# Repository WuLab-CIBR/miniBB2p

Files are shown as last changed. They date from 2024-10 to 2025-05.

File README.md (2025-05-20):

# miniature Bessel-beam two-photon microscope (miniBB2p)
## Description
This repository includes the optical design files, technical drawings, assembly protocol, and code for hardware control of miniBB2p. miniBB2p is a head-mounted miniature Bessel-beam two-photon microscope, published in Qian, et al.,"High-throughput two-photon volumetric brain imaging in freely moving mice (2024)". The miniBB2p is characterized by its lightweight design, reduced tethering stress, simple optics, and maximized fluorescence collection efficiency. 
## Contents
1) [Optical design files](https://github.com/WuLab-CIBR/miniBB2p/tree/main/Supplementary%20Data/Zemax)
   
    Bessel beam simplifies the optical design in miniBB2p:
   
   

2) Technical drawings ([2D models](https://github.com/WuLab-CIBR/miniBB2p/tree/main/Supplementary%20Data/2D%20model) and [3D models](https://github.com/WuLab-CIBR/miniBB2p/tree/main/Supplementary%20Data/3D%20model))

     3D models (and 2D drawings for custom components) of all components for bulding a miniBB2p headpiece.
    3D model

3) [Assembly protocol](https://github.com/WuLab-CIBR/miniBB2p/tree/main/Supplementary%20Data/Assembly%20protocol)

     This protocol includes all steps to assemble a miniBB2p headpiece. Each protocol starts with a short-list of main reagents and tools needed, followed by an overview schematic of the module, and a table with the main products.  2D drawings for custom components used in assembly setup are also attached.

4) [Code for hardware control](https://github.com/WuLab-CIBR/miniBB2p/tree/main/Supplementary%20Data/Code)

     An application to control the miniBB2p, set the imaging parameter, and save the imaging data. The application was written with Matlab.

## References
  Qian, L., Liu, Y., Chen, Y., & Wu, J. (2024). High-throughput two-photon volumetric brain imaging in freely moving mice. bioRxiv, 2024-10.
  DOI:https://doi.org/10.1101/2024.10.13.618106

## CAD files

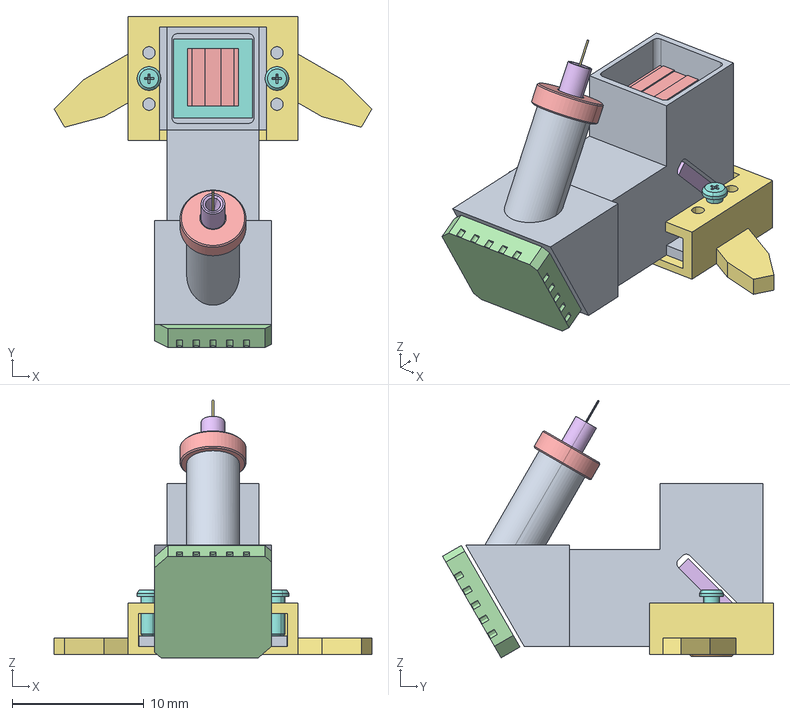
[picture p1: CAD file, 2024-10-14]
Supplementary Data/3D model/miniBB2p.stp
24.1 x 25.1 x 19.5 mm

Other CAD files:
Supplementary Data/Assembly protocol/Technical drawings of the assembly setup/Main Frame Holder.dwg
Supplementary Data/2D model/Main Frame.dwg
Supplementary Data/2D model/Scan and Tube Lens Holder.dwg
Supplementary Data/Assembly protocol/Technical drawings of the assembly setup/MEMS Mirror Holder.dwg
Supplementary Data/2D model/Objective Holder.dwg
Supplementary Data/Assembly protocol/Technical drawings of the assembly setup/Collimator Holder.dwg
Supplementary Data/2D model/Collimator Lens Holder.dwg
Supplementary Data/2D model/Baseplate.dwg

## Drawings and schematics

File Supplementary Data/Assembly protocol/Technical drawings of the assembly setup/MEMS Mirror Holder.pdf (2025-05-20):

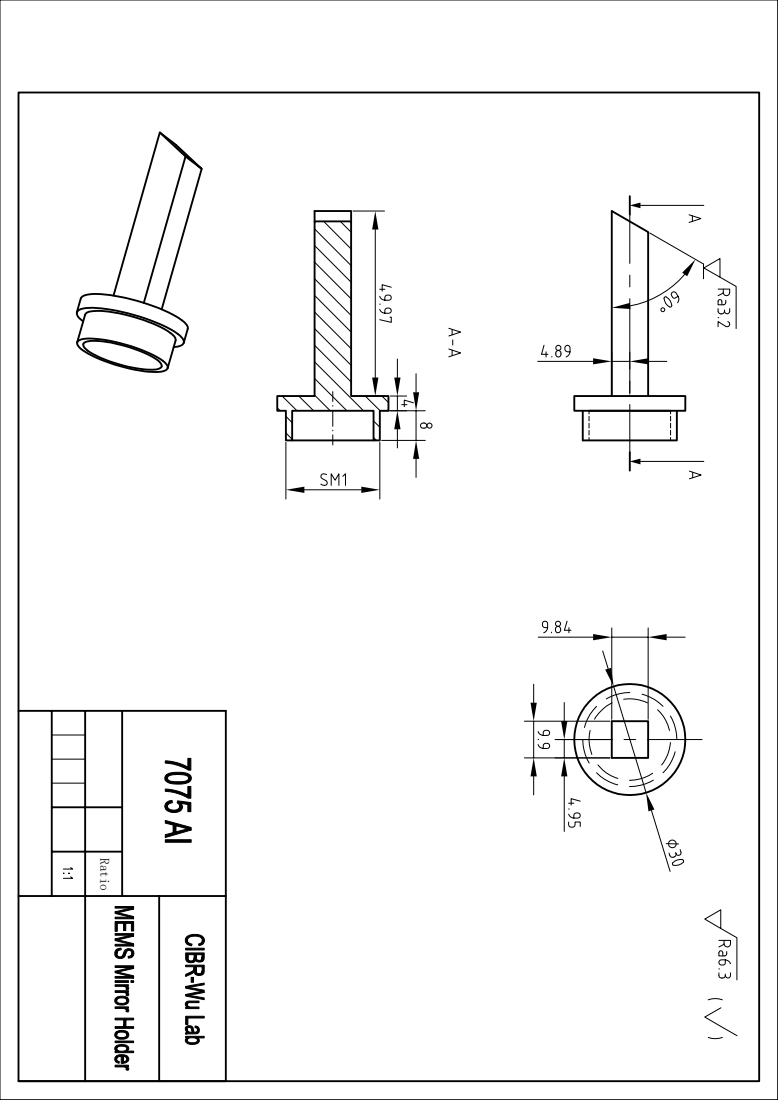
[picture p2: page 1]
Ratio

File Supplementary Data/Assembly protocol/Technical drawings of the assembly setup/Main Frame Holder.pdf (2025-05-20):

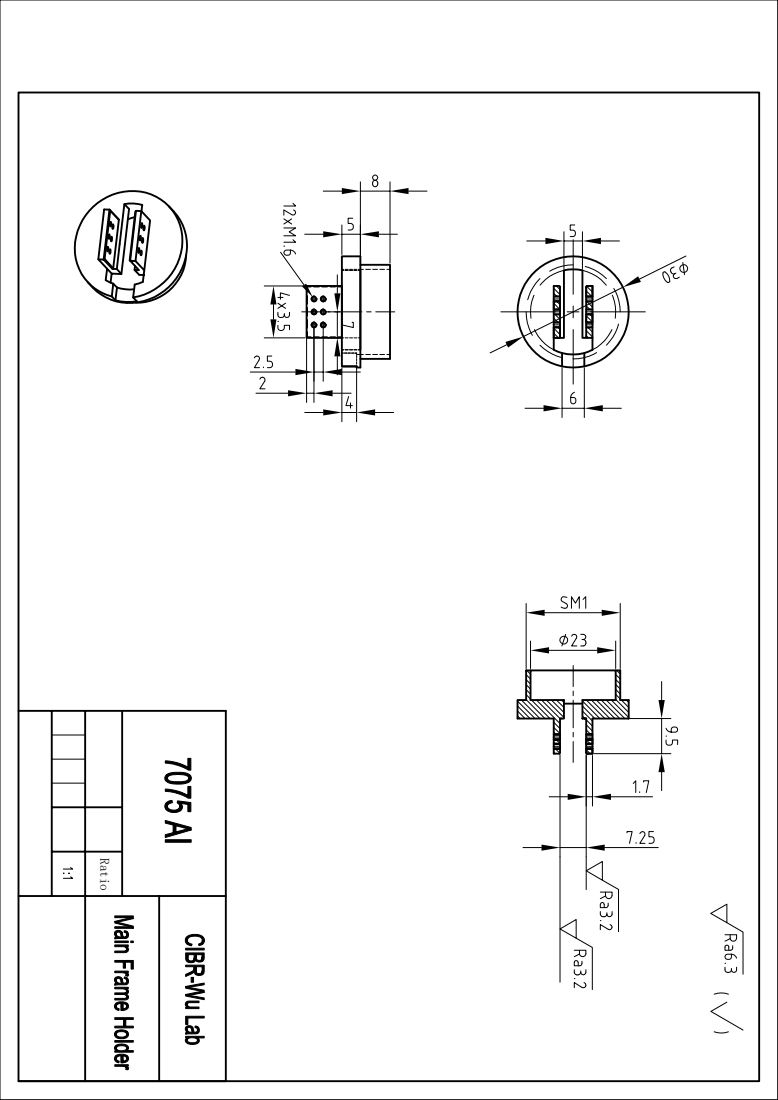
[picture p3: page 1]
Ratio

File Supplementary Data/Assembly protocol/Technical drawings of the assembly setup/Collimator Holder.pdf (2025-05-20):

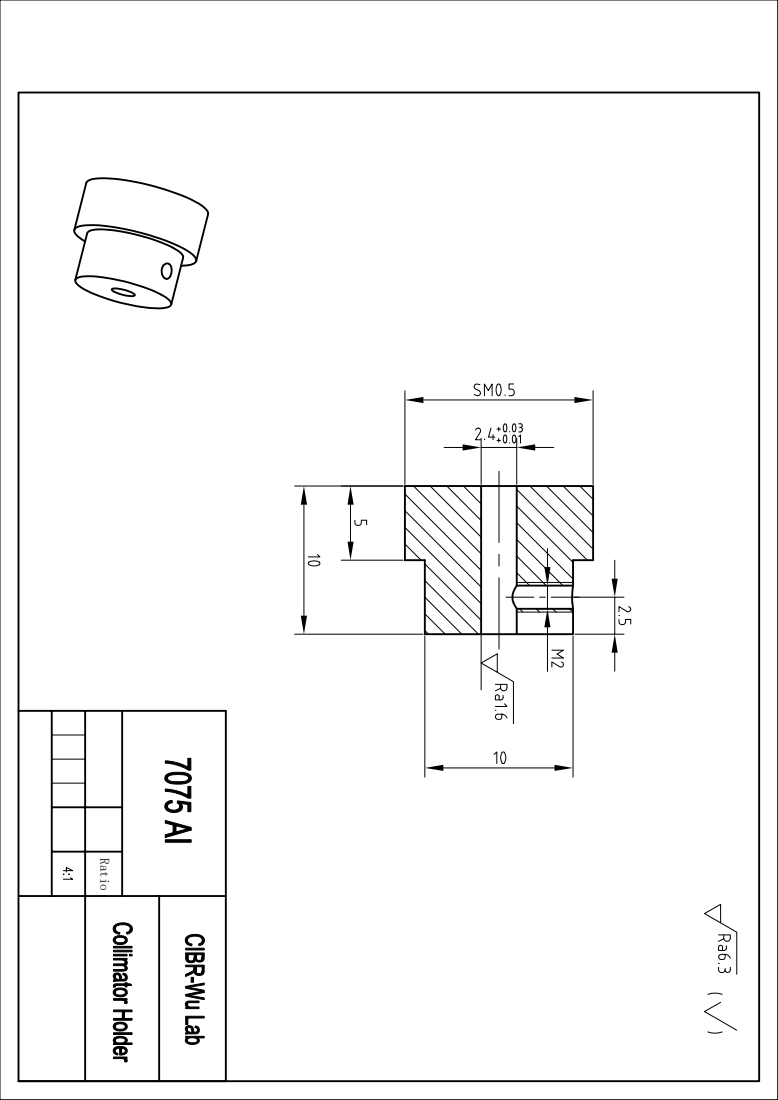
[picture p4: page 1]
Ratio

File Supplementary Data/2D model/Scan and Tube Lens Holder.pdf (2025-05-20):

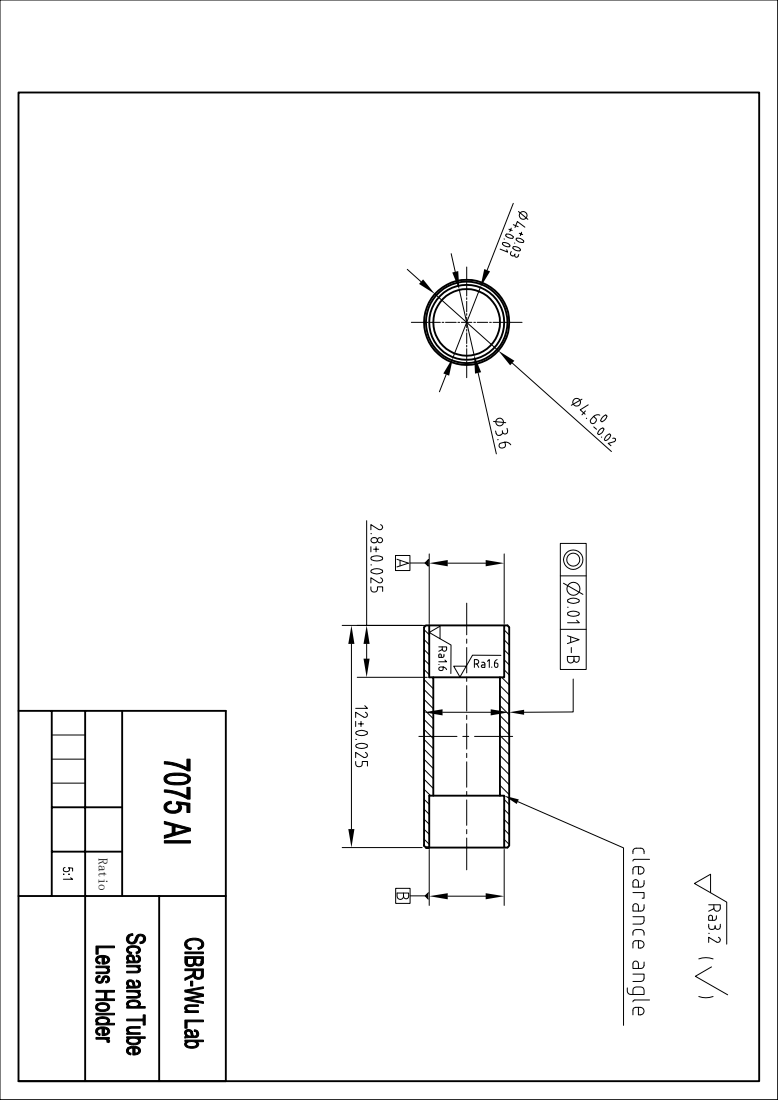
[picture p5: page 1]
Ratio

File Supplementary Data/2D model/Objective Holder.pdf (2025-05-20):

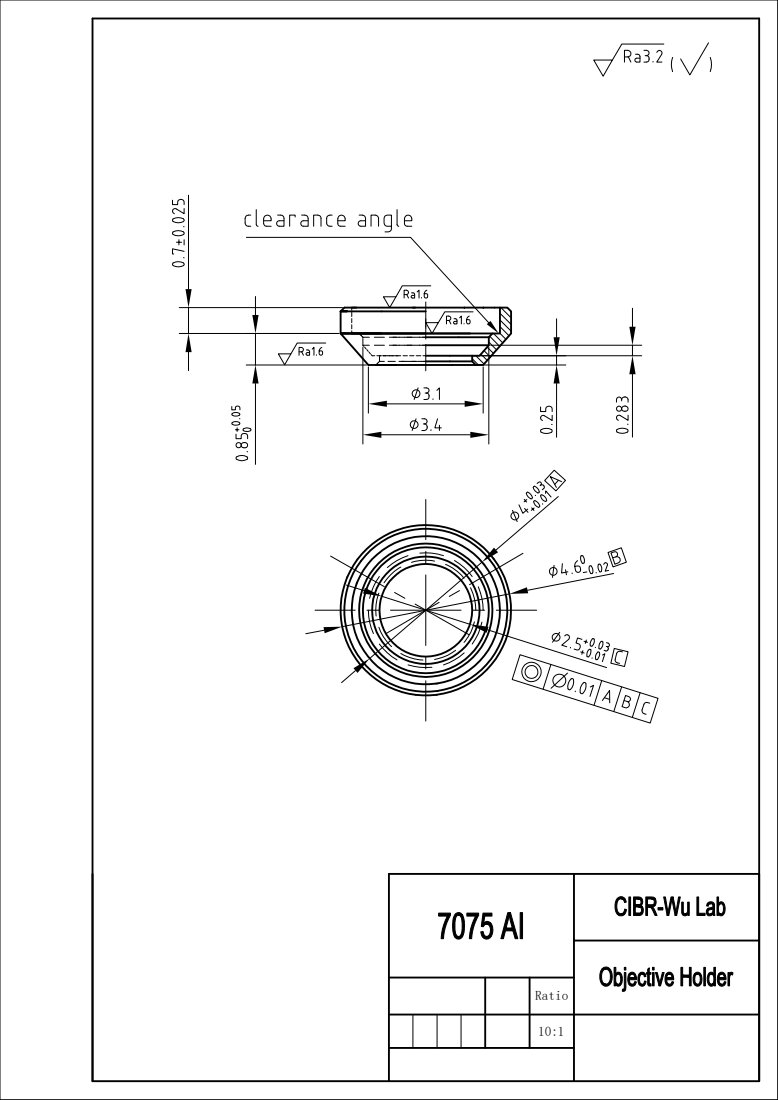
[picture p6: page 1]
Ratio

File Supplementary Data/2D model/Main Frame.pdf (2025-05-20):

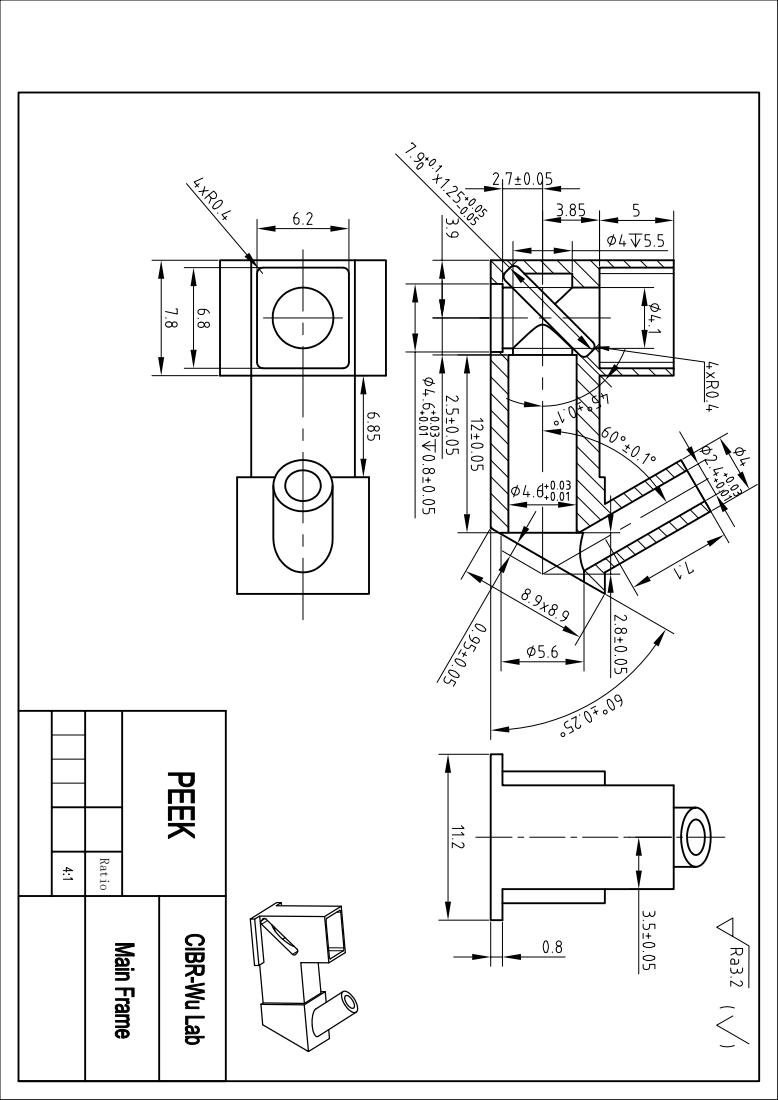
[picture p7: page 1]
Ratio

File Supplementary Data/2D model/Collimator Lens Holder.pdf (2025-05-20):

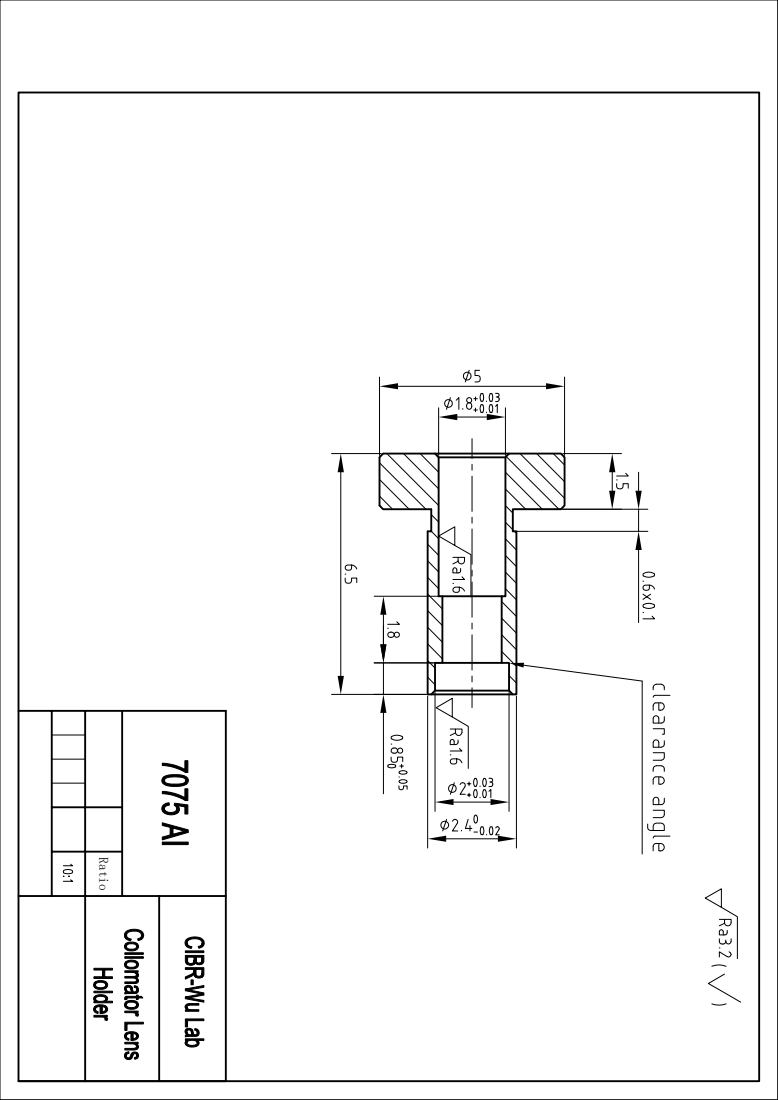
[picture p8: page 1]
Ratio

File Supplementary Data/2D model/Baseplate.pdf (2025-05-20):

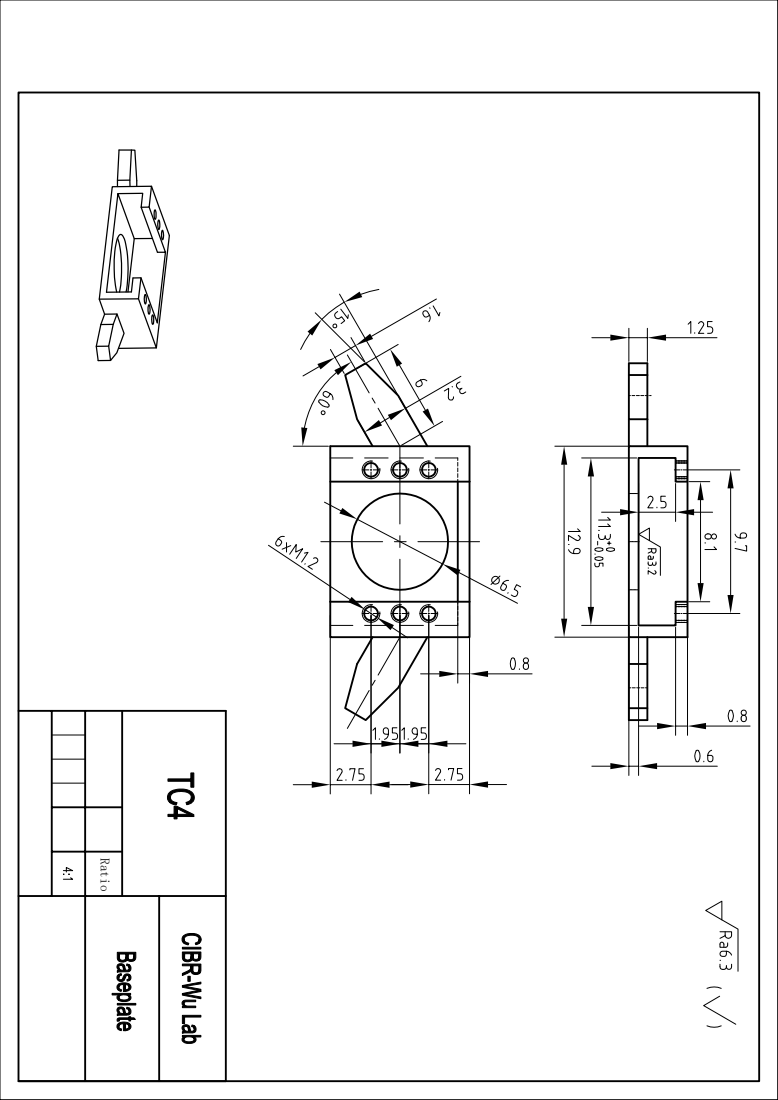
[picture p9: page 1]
Ratio

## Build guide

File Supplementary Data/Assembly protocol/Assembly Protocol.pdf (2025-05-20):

### A protocol for the assembly of miniBB2p headpiece

Part A: Evaluating the micro-axicon fabricated on the fiber tip

Reagents:

⚫ | Air duster
⚫ | Lens cleaning wipe
⚫ | 100% ethanol

Equipment:

⚫ | ~1.5-meter LMA-12 fiber (NKT Photonics) with customized micro-axicon tip (Comcore)
⚫ | Tweezers
⚫ | Fiber stripping tool (T06S13, Thorlabs)
⚫ | Fiber cleaver (CT-101, Fujikura)
⚫ | Stereoscope (M125C, Leica)
⚫ | Beam profiler (CMOS-1202, CINOGY Technologies)
⚫ | Power meter (PM130D, Thorlabs)
⚫ | Others (Table 1)

Table 1 Main components used to evaluate the micro-axicon fabricated on the fiber tip

Component Number | Component Name | Part Number | Amount | Company
#1 | Post-Mountable Fiber Clamp | T711/M-250 | 1 | Thorlabs

#2 | 3-Axis Stage | MAX313D/M | 1 | Thorlabs

#3 | Fiber Holder for 3-Axis Stage | HFV002 | 1 | Thorlabs

Procedure:

Step 1. Examine the fiber tip under a stereoscope to confirm the micro-axicon's quality (Figure 1.1). Should dust be present, carefully clean the tip with either an air duster or a lens cleaning wipe.

Caution! The fiber tip is fragile. Clean it with extreme caution, particularly when using a lens cleaning wipe moistened with 100% ethanol.

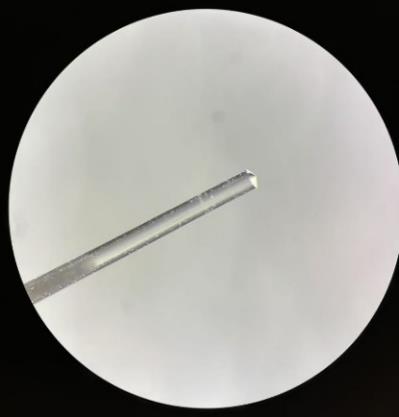
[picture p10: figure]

Figure 1.1 Visual inspection of the fiber tip under the stereoscope

Step 2. Remove about 3–4 cm protecting claddings of the fiber on the other end by using a fiber stripping tool. Then clean the exposed area with a lens tissue moistened with 100% ethanol.
Step 3. Cleave the fiber end using the fiber cleaver (Figure 1.2).

Caution! In Steps 2–3, only handle the fiber end without micro-axicon and avoid any collision/scratch of micro-axicon tip.

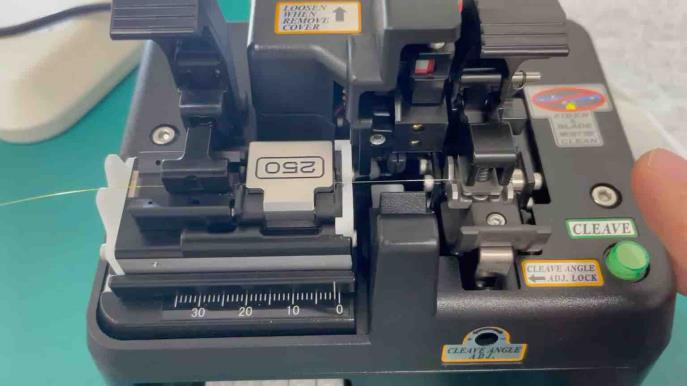
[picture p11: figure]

Figure 1.2 Cleave the fiber end

Step 4. Mount the fiber end with micro-axicon using fiber clamp (#1) and place a power meter behind the micro-axicon. Secure the other end of the fiber on the fiber holder (#2) and mount the holder into a 3-axis stage (#3) (Figure 1.3). Adjust the stage until the output power reaches about several mW.

Note! We do not need to maximize the laser power coupled into the fiber at this step, a power level of several mW is sufficient for the evaluation.

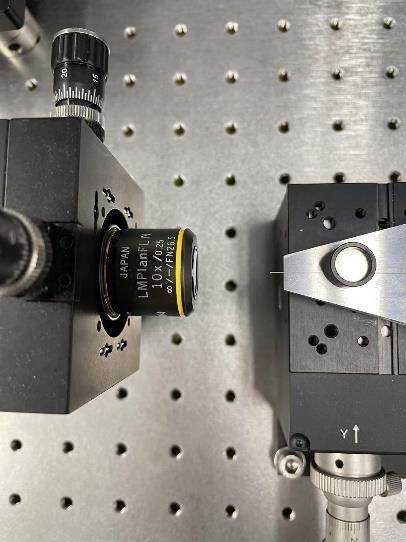
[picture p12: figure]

Figure 1.3 Fiber coupling setup

Step 5. Replace the power meter with the beam profiler in Step 4. Monitor the laser output from the micro-axicon tip, and make sure that a uniform ring could be observed (left panel in Figure 1.4).

Troubleshooting! If the output is not a uniform ring (right panel in Figure 1.4), double-check if there is any dust on the micro-axicon tip, or if the end of the micro-axicon tip is clamped too tight. If the problem still exists, check the manufacture quality of the micro-axicon tip.

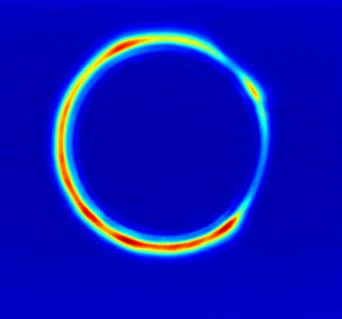
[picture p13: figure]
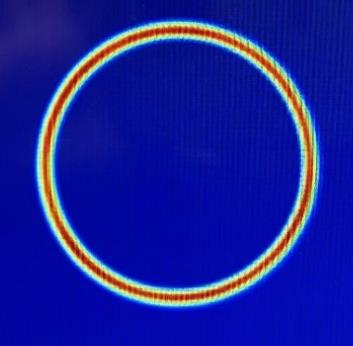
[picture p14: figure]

Figure 1.4 Representative images showing ring beam with high (left) and low (right) qualities.

Part B: Assembling the fiber collimator

Reagents:

⚫ | Air duster
⚫ | Lens cleaning wipe
⚫ | 100% ethanol
⚫ | UV-Curing Optical Adhesives (NOA61, Thorlabs)
⚫ | Black epoxy glue (9005B, LEAFTOP)

Equipment:

⚫ | Tweezers
⚫ | UV lamp
⚫ | Ultrasonic cleaner
⚫ | ~1.5-meter length LMA-12 fiber (NKT Photonics) with fabricated micro-axicon tip (Comcore)
⚫ | Stereoscope (M125C, Leica)
⚫ | NIR Detector Card (VRC4, Thorlabs)
⚫ | Video camera
⚫ | Beam profiler (CMOS-1202, CINOGY Technologies)
⚫ | Others (Table 2)

Table 2 Main components of the fiber collimating setup

Component Number | Component Name | Part Number | Amount | Company
#4 | Glass Flange | TUB-1.8x6-0.127 | 1 | Sunlight

#5 | Collimating Lens Holder | / | 1 | Customized

#6 | Collimating Lens | 45-956 | 1 | Edmund

#2 and #7 | 3-Axis Stage | MAX313D/M | 2 | Thorlabs

#8 | Adjustable Fiber Clamp | HFF001 | 1 | Thorlabs

#9 | Compatible Flexure Stage Mount | HCS020 | 1 | Thorlabs

#10 | Collimator Holder | / | 1 | Customized

#11 | Fixed Mounting Bracket | AMA007/M | 1 | Thorlabs

Procedure:

Step 6. Clean the glass flange (#4) and collimating lens holder (#5) in an ultrasonic cleaner for 15 minutes, and spray all the cleaned components with air duster.
Step 7. Visually inspect the fiber end with micro-axicon if the length of the removed protective cladding is longer than the length of glass flange.

Note! A piece of protective cladding at the fiber end was removed during micro-axicon fabricating. Please customize this length in advance, as remove of the protective cladding near micro-axicon may lead to damage of the micro-axicon tip. If the glass flange is longer, we suggest cutting the glass flange instead of re-removing protective cladding of the fiber.

Step 8. Carefully slide the glass flange on the micro-axicon tip end of the fiber with a tweezer under the stereoscope, until micro-axicon tip is slightly sticking out at the other end of the flange (Figure 2.1).

Caution! Insertion itself may break down the micro-axicon tip.

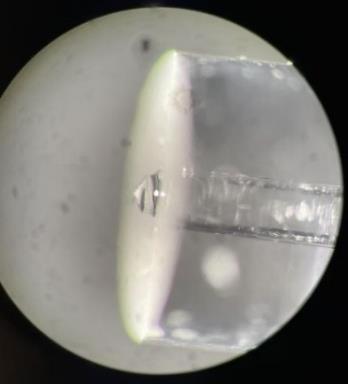
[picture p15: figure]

Figure 2.1 Photo of the fiber inserted into glass flange

Step 9. Add UV-curable adhesive to the funnel at the root of the glass flange (Figure 2.2). Wait until adhesive fill the gap between the glass and fiber, then cure the adhesive with UV lamp for ~1 min.

Caution! Adhesive should be added slowly, and the filling process should be monitored under the stereoscope to avoid the micro-axicon tip contaminated by the adhesive.

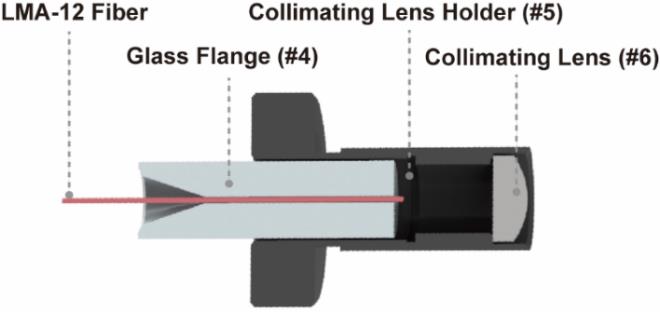
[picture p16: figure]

Figure 2.2 Schematic of the fiber collimator

Note! We need to double check the laser output from the micro-axicon tip by following a protocol similar to that in Steps 4–5. The output ring pattern should be still uniform.

Step 10. Fix the collimating lens (#6) into the lens holder (#5) with UV-curable adhesive following a protocol similar to Step 9 (Figure 2.2).

Caution! Pay attention not to get adhesive on the surface of the collimating lens. Apply glue only to the gap between the collimating lens and lens holder.

Step 11. Set up the fiber coupling stage according to Figure 2.3. Align the V-groove of the adjustable fiber clamp (#8) and the center of the collimator holder (#10) by adjusting the 3-axis stage (#7).

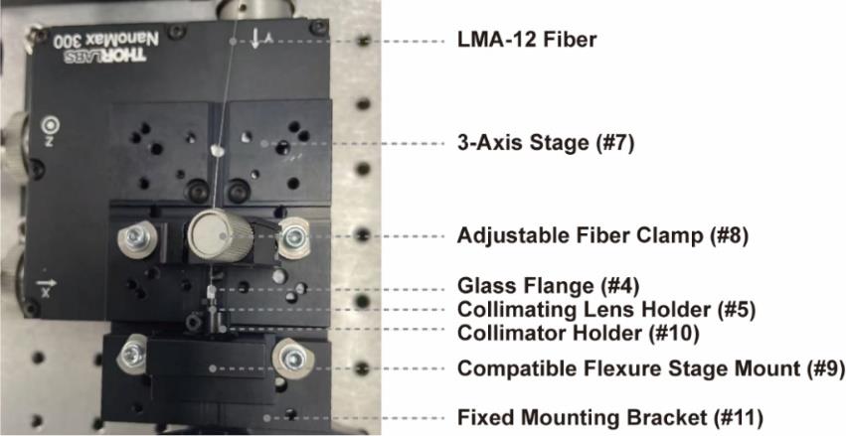
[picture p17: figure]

Figure 2.3 Fiber coupling stage

Step 12. Open the adjustable fiber clamp and carefully insert the glass flange (with fiber) into the collimating lens holder.

Caution! Insertion itself may break down the fiber. Insert the glass flange to the bottom of the collimating lens holder, and then move glass flange back for about 1–2 mm to reserve enough space for further adjustment.

Note! If a longer protruding tip was prepared in Steps 8–9, do not insert the glass flange all the way to the bottom of the collimating lens holder in this step. This prevents the micro-axicon tip from colliding with the collimating lens.

Step 13. Secure the LMA-12 fiber by tightening the adjustable fiber clamp (#8). Ensure the glass flange can move smoothly back and forth within the hole of the collimating lens holder by adjusting the 3-axis stage.

Note! If the glass flange cannot move smoothly, make slight adjustments using the 3-axis stage. Exercise caution during adjustment to avoid fiber damage. Loosen the adjustable fiber clamp if a large adjustment is required.

Step 14. Mount the other end of the fiber onto the second 3-axis stage and couple the laser into the fiber following a protocol similar to Step 4 (Figure 2.4).

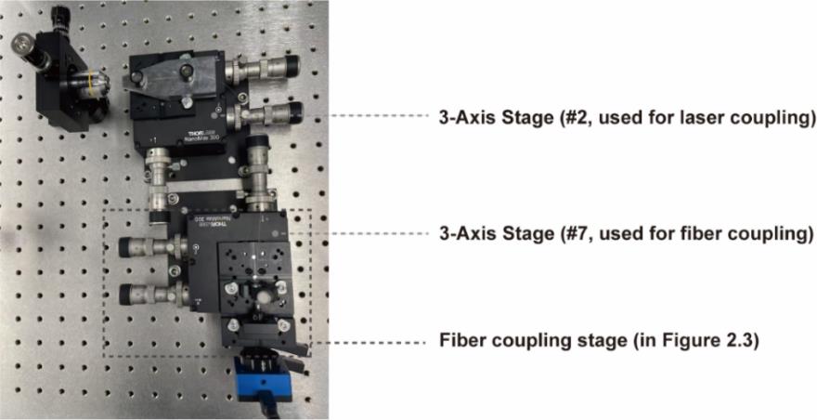
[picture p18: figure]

Figure 2.4 Two 3-axis stages used in the setup; a short-length fiber used here for visualization.

Step 15. Carefully adjusting the distance between the glass flange and collimating lens using the 3-axis stage until a near-collimated ring pattern could be seen with the NIR detector card (Figure 2.5).

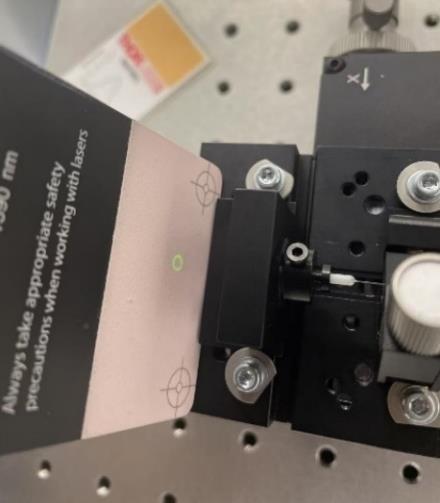
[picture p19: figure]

Figure 2.5 Visual inspection of the beam with a NIR detector card

Step 16. Replace the NIR detector card with a camera in Step 15. Finely adjust the 3-axis stage until the ring pattern’s diameter remains constant when moving the camera forward and backward.

Note! Since the ring pattern is only observable within a very short working distance (Figure 2.6), position the camera sensor as close as possible to the fiber tip.

Figure 2.6 Simulation result of the collimated Bessel ring derived from the collimator.

Step 17. Firmly attach the glass flange to the collimating lens holder using black epoxy glue.

Caution! Avoid contact with both the fiber and glass flange during adhesive application, as physical disturbance may alter the critical distance between the fiber tip and collimating lens.

Step 18. After the epoxy has fully cured, gently detach the collimating lens holder (#5) from the collimator holder (#10) and verify the quality of the ring pattern from the collimator.

Part C: Assembling other optical and electrical components

Reagents:

⚫ | Air duster
⚫ | Lens cleaning wipe
⚫ | 100% ethanol
⚫ | UV-Curing Optical Adhesives (NOA61, Thorlabs)
⚫ | Black epoxy glue (9005B, LEAFTOP)
⚫ | Soldering tip thinner & cleaner

Equipment:

⚫ | Tweezers
⚫ | Scissor
⚫ | Stripping tool
⚫ | Soldering iron
⚫ | UV lamp
⚫ | Ultrasonic cleaner
⚫ | Stereoscope (M125C, Leica)
⚫ | Main components of the scan and tube lens setup (Table 3.1)
⚫ | Main components of the objective setup (Table 3.2)
⚫ | Main components of the MEMS mirror setup (Table 3.3)
⚫ | Main components of the SiPM detector setup (Table 3.4)

Table 3.1 Main components of the scan and tube lens setup

Component Number | Component Name | Part Number | Amount | Company
#12 | Scan and Tube Lens Holder | / | 1 | Customized

#13 | Scan and Tube Lenses | 48-704 | 4 | Edmund

Table 3.2 Main components of the objective setup

Component Number | Component Name | Part Number | Amount | Company
#14 | Objective Holder | / | 1 | Customized

#15 | Objective Lens (φ2.5 mm) | 65-300 | 1 | Edmund

#16 | Objective Lens (φ4.0 mm) | 47-850 | 1 | Edmund

Table 3.3 Main components of the MEMS mirror setup

Component Number | Component Name | Part Number | Amount | Company
#17 | MEMS Mirror | A3I12.2-1200AL | 1 | Mirrorcle

#18 | MEMS PCB | / | 1 | Customized

#19 | Multi-Core Cable | EN4C-FEP | ~1.5 m | METOP

Table 3.4 Main components of the SiPM detector setup

Component Number | Component Name | Part Number | Amount | Company
#20 | SiPM Detector | S13360-3075PE | 1 | Hamamatsu

#21 | Coaxial Cable | 44AWG | ~1.5 m | METOP

#22 | Filter (size of 6 × 6 mm² ) | FGB37-A | 1 | Thorlabs

Procedure:

Step 19. Clean the mechanical components #12 and #14, following the same protocol as Step 6.

Part C1: Assembling scan and tube lens

Step 20. Install the four lenses (#13) sequentially into the scan and tube lens holder (#12) using UV-curable adhesive, following the same protocol as Step 10 (Figure 3.1)

Note! The scan and tube lenses theoretically form an ideal 4f system in the design. However, in practice, manufacturing tolerances of both the lenses and holder may cause slight convergence or divergence in the output beam. This primarily affects the working distance of the objective lens.

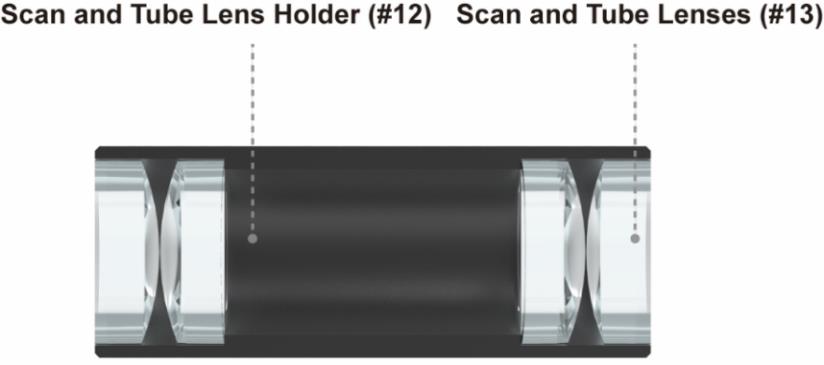
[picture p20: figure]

Figure 3.1 Schematic of the scan and tube lens

Part C2: Assembling objective

Step 21. Install the lens (#15) into the objective holder (#14) using UV-curable adhesive, following the same protocol as Step 20 (Figure 3.2).

Caution! Seal the objective by applying sufficient UV-curable adhesive to fill the interface gap between the lens and its holder.

Step 22. Install the second lens (#16) into the objective holder (#14) using UV-curable adhesive, following the same protocol as Step 20 (Figure 3.2).

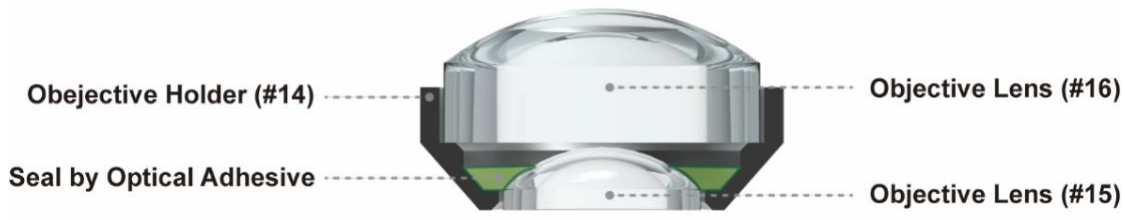
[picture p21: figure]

Figure 3.2 Schematic of the objective

Part C3: Assembling MEMS mirror

Step 23. Solder the MEMS PCB (#18) to the base of the MEMS mirror (#17) and the multi-core cable (#19) to the MEMS PCB (#18) as shown in Figure 3.3. (Zong et al. have detailed the soldering methods in their work, https://doi.org/10.1016/j.cell.2022.02.017).

Caution! Do not remove the protective glass of the MEMS mirror at this step.

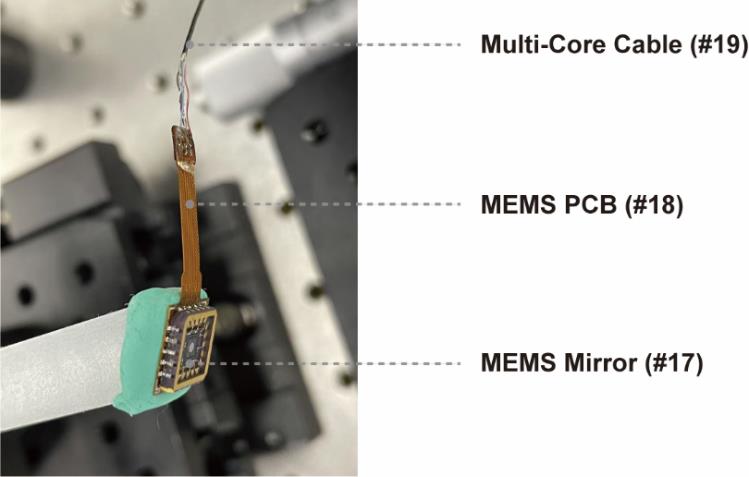
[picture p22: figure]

Figure 3.3 Photo of the MEMS mirror attached to its holder

Part C4: Assembling SiPM detector

Step 24. Connect the coaxial cable (#21) to the SiPM detector (#20) using similar soldering protocol described in Step 23.
Step 25. Position the SiPM detector with its photosensitive surface facing downward onto the center of the filter (#22), then secure it using UV-curable adhesive.

Caution! Only add a minimal amount of adhesive at the edge of the SiPM detector to prevent seepage into the detector-filter interface, which could contaminate the photosensitive surface.

Step 26. Apply black epoxy adhesive around the perimeter of the SiPM detector (Figure 3.4).

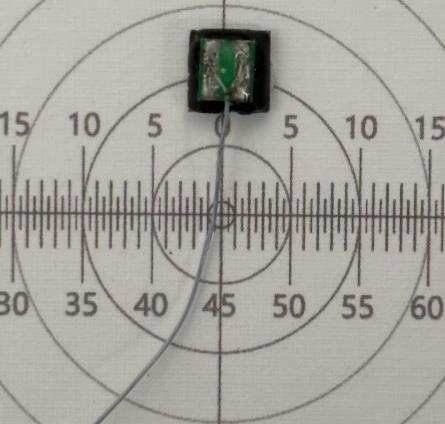
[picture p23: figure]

Figure 3.4 Fixing the SiPM detector onto the filter using black epoxy adhesive

Step 27. Apply black epoxy adhesive on the top of the SiPM detector (Figure 3.5).

Note! Steps 26–27 are critical for preventing scattered light from entering the SiPM detector.

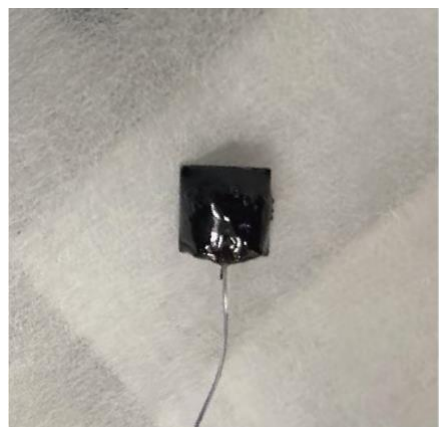
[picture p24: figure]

Figure 3.5 Sealing the SiPM detector using black epoxy adhesive

Part D: Assembling the main body of the miniBB2p headpiece.

Reagents:

⚫ | Air duster
⚫ | Lens cleaning wipe
⚫ | 100% ethanol
⚫ | UV-Curing Optical Adhesives (NOA61, Thorlabs)
⚫ | Black epoxy glue (9005B, LEAFTOP)
⚫ | Black plasticine
⚫ | Black tape
⚫ | Tack-It (Faber Castle)

Equipment:

⚫ | Tweezers
⚫ | UV lamp
⚫ | Ultrasonic cleaner
⚫ | Stereoscope (M125C, Leica)
⚫ | Power meter (PM130D, Thorlabs)
⚫ | Optical mirror (UM10-AG, Thorlabs)
⚫ | NIR Detector Card (VRC4, Thorlabs)
⚫ | Oscilloscope (Tektronix, MDO34 3-BW-200)
⚫ | Fluorescent beads slide
⚫ | Fiber collimator (assembled in Part B)
⚫ | Scan and tube lens (assembled in Part C1)
⚫ | Objective (assembled in Part C2)
⚫ | MEMS mirror (assembled in Part C3)
⚫ | SiPM detector (assembled in Part C4)
⚫ | Main components of the main body setup (Table 4.1)

Table 4.1 Main components of the main body setup

Component Number | Component Name | Part Number | Amount | Company
#23 | Main Frame | / | 1 | Customized

#24 | Dichroic Mirror (size of 7 × 7 mm² ) | DMR-805SP | 1 | LBTEK

#25 | Filter (size of 6 × 6 mm² ) | FIL-800 | 1 | Sunlight

#26 | Main Frame Holder | / | 1 | Customized

#27 | MEMS Mirror Holder | / | 1 | Customized

#28 | 6-Axis Kinematic Mount (Frame) | K6XS | 1 | Thorlabs

#29 | Rotation Stage | XRR1/M | 1 | Thorlabs

#30 | Dovetail Rail | XR25DR3 | 1 | Thorlabs

#31 | 6-Axis Kinematic Mount (MEMS) | K6XS | 1 | Thorlabs

#32 | XY Translation Stage | PT1/M | 2 | Thorlabs

#33 | Mounting Adapter | PT101/M | 1 | Thorlabs

#34 | Single-Axis Translation Stage | PT1/M | 1 | Thorlabs

Procedure:

Step 28. Clean mechanical components #23, #26, and #27 following the same protocol as Step 6.

Part D1: Assembling optical components

Step 29. Assemble the dichroic mirror (#24), the scan and tube lens (assembled in Part C1), and the objective lens (assembled in Part C2) into the main frame (#23) in sequence, using UV-curable adhesive. Assemble the filter (#25) into the main frame using black epoxy adhesive.

Caution! The coated surface of the dichroic mirror and filter should face downward. When inserting the dichroic mirror into the narrow slit on the main frame, take care to avoid damaging the coated surface. Seal the slit using black tape or black epoxy adhesive.

Part D2: Assembling and evaluating the SiPM detector

Step 30. After the epoxy has fully cured, temporarily secure the SiPM detector (assembled in Part C4) into the main frame using black plasticine.
Step 31. Mount the main frame and align the free-space laser beam with the principal optic axis of the scan and tube lens. A focal spot can be observed after the objective using the NIR detector card.

Note! The beam can be aligned imperfectly at this step.

Step 32. Place an optical mirror behind the objective and increase the laser power to a high level (we used 100 mW post-objective).
Step 33. Turn off all the light in the room, and monitor the signal of the SiPM detector using an oscilloscope. Similar signal levels should be observed whether we turn on or off the laser.

Note! In Steps 32–33, the 920-nm laser reflected from the mirror simulates the scattered/reflected excitation light during imaging, which should be fully blocked by the filters.

Troubleshooting! If an increasing signal level is observed when turning on the laser (indicating that the gaps in Steps 26 and 29 were not fully filled with black epoxy adhesive), re-sealing these gaps with black epoxy adhesive is critical to ensure effective background light rejection.

Part D3: Assembling the MEMS mirror

Step 35. Set up the assembling stage (Figure 4.1). Align the center of two 6-axis kinematic mounts (#28 and #31) by screwing z-axis adjustments of the mounts.

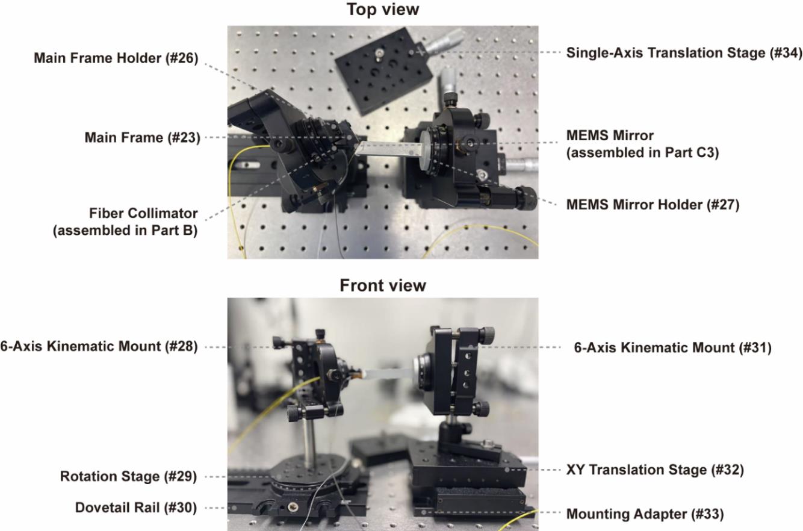
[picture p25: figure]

Figure 4.1 Assembling stage

Step 36. Unlock the dovetail locking screw of the rotation stage (#29) and move the rotation stage away from the MEMS mirror holder (#27). Insert the fiber collimator (assembled in Part B), through the 6-axis kinematic mount (#28), to the main frame. Fix the main frame to the main frame holder (#26) using screws.
Step 37. Mount the MEMS mirror (assembled in Part C3) onto the MEMS mirror holder by using Tack-It (Figure 4.1). Carefully remove the protective glass of the MEMS mirror with a tweezer.

Caution! Pay attention to mounting direction of the MEMS mirror.

Step 38. Move the rotation stage close to the MEMS mirror. Align the mounting surface of the main frame to the package of the MEMS mirror (Figure 4.2) by adjusting the 6-axis kinematic mount (#28) and rotation stage (#29). Lock the dovetail locking screw of the rotation stage.

Caution! The rotation stage needs to be slightly moved forward or backward several times during aligning.

Caution! After this step, keep all the pitch, yaw, and rotation adjustment unchanged, and only adjust x-, y-, or z-translation.

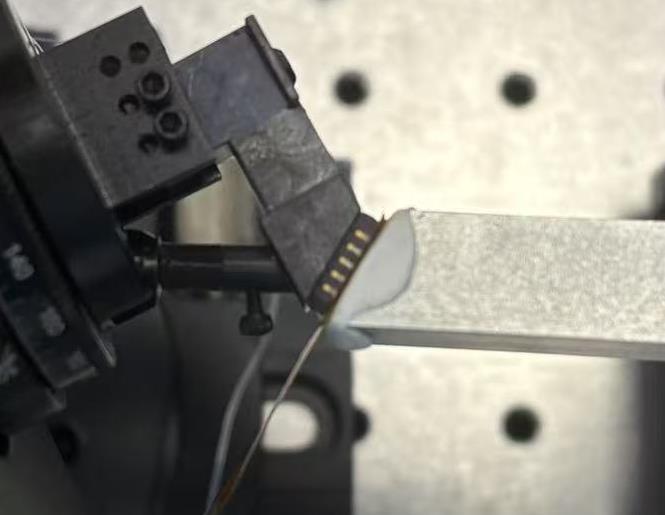
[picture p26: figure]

Figure 4.2 Align the main frame and MEMS mirror

Step 39. Couple the laser into the fiber following the same protocol as Step 4, monitor the beam after the objective using the NIR detector card, and adjust the 6-axis kinematic mount (#31) until the outgoing laser is fully ring-shaped and not trimmed (Figure 4.3).

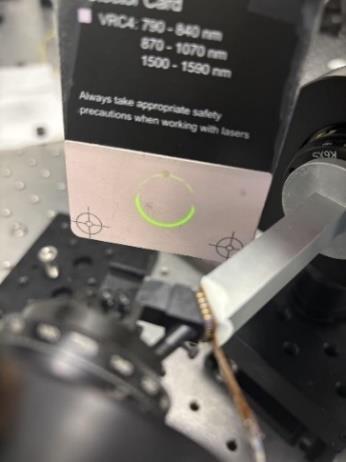
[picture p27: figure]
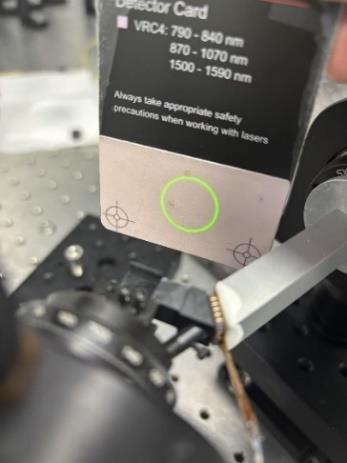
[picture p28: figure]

Figure 4.3 Trimmed (left) and untrimmed ring beam (right)

Step 40. Place a fluorescent bead slide on the single -axis translation stage (#34) (Figure 4.4).

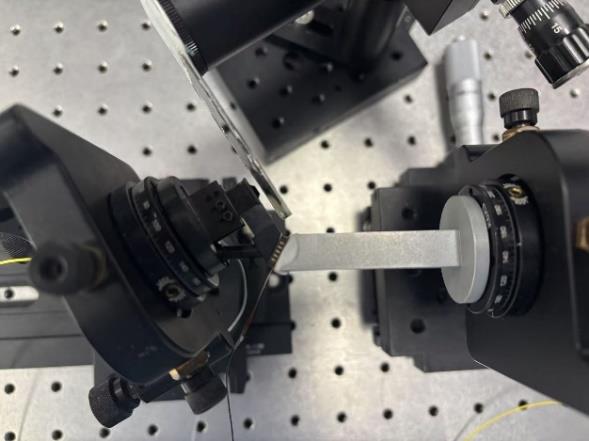
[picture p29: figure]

Figure 4.4 Imaging fluorescent beads on a slide

Step 41. Fill the imaging medium between the objective and slide. Turn off all lights in the room, then adjust the single -axis translation stage (#34) to position the slide at the focal plane of the miniBB2p.
Step 42. Slightly adjust the XY translation stage (#32) and 6-axis kinematic mount (#31) until sharp spots (point spread functions) could be observed across the field of view (Figure 4.5).

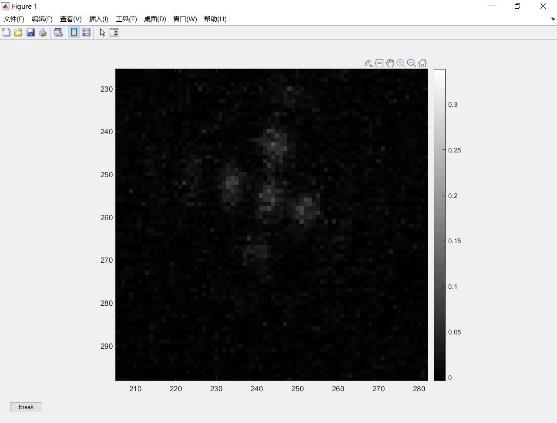
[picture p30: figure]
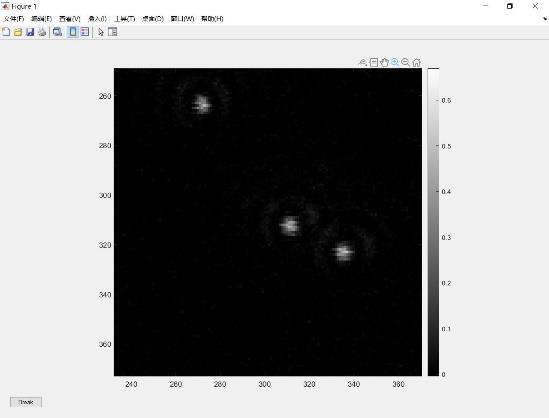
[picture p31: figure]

Figure 4.5 Representative images showing blurred (left) and sharp spots (right).

Step 43. Lock all the screws of the mounts and stages. Apply a small amount of UV-curable adhesive to the gap between the MEMS package and the attached main frame surface (Figure 4.6), following the protocol described in Step 10.

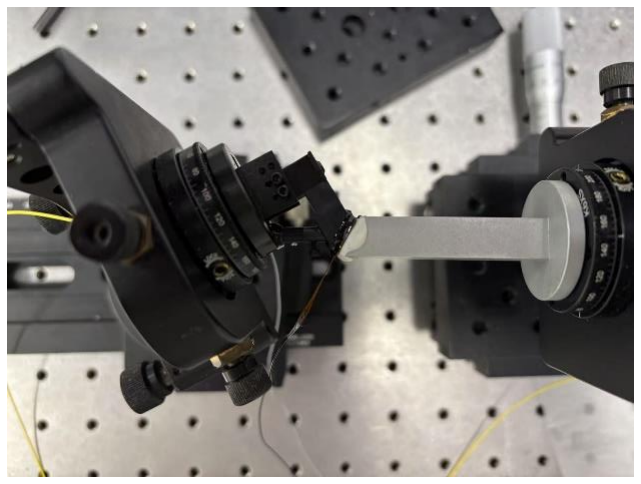
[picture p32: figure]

Figure 4.6 Bond the MEMS mirror to the main frame.

Caution! Avoid using too much adhesive, as excess adhesive can bond to the MEMS surface and cause damage.

Step 44. Apply black epoxy adhesive around the gap and allow at least 24 hours curing time for the MEMS-to-main frame bond to stabilize (Figure 4.6).

Caution! Take care not to adjust any mounts or stages during Steps 43–44.

Step 45. After the black epoxy adhesive has cured, separate the MEMS mirror from its holder by removing Tack-It, remove the fiber collimator from the main frame, and detach the main frame from its holder.

Part E: Fiber protecting and connecting

Reagents:

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

Equipment:

⚫ | Scissor
⚫ | Tweezers
⚫ | UV lamp
⚫ | Stereoscope (M125C, Leica)
⚫ | Fiber stripping tool (T06S13, Thorlabs)
⚫ | Power meter (PM130D, Thorlabs)
⚫ | NIR Detector Card (VRC4, Thorlabs)
⚫ | Fiber collimator (assembled in Part B)
⚫ | Main components of the fiber protecting and connecting setup (Table 1)

Table 5.1 Main components of the fiber protecting and connecting setup

Component Number | Component Name | Part Number | Amount | Company
#35 | Furcation Tubing | FT900Y | ~1 m | Thorlabs

#36 | Fiber Connector | 30126C9 | 1 | Thorlabs

#37 | Connectorized-Fiber Holder | OFB02-FPC2 | 1 | LBTEK

Procedure:

Step 46. Carefully insert the fiber into the furcation tubing (#34), advancing it until the furcation tubing reaches the collimating lens holder (#5).

Caution! Double-check the fiber end prepared in Step 3. If the surface is not flat, re-cut the fiber using a protocol similar to Step 3 before insertion.

Caution! First measure both the fiber and furcation tubing lengths. The furcation tubing should be ~4 cm shorter than the fiber for proper assembly with fiber connector (#36).

Step 47. Secure the furcation tubing to the collimating lens holder using black epoxy adhesive.
Step 48. Assemble the fiber connector (#36) according to the Thorlabs FN96A guide (Chapter 2).

Caution! The LMA-12 fiber cannot be polished after connector assembly, so ensure the stripped fiber has the appropriate length before assembling the connector.

Step 49. Secure the other end of the furcation tubing to the connector boot using UV-curable adhesive.

Step 50. Mount the assembled fiber onto the connectorized-fiber holder (#37), and optimize the laser-to-fiber coupling using the protocol described in Step 4 (Figure 5.1).

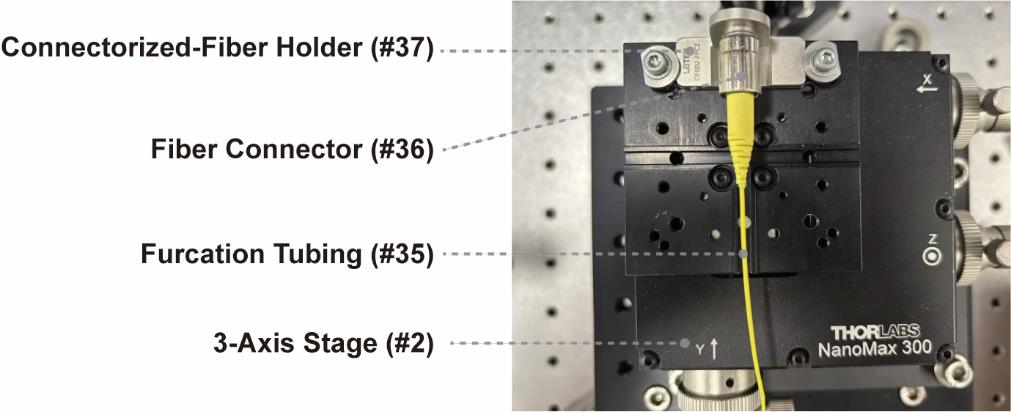
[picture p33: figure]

Figure 5.1 Mount the assembled fiber onto the connectorized-fiber holder.

Step 51. Reinsert the fiber collimator into the main frame and secure it using black epoxy adhesive.

Caution! Verify the imaging performance before applying the adhesive.

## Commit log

2025-05-20 Technical drawings used in the assembly setup
2025-05-20 Assembly Protocol
2025-05-20 The optical design files, technical drawings, assembly protocol, and code for hardware control of miniBB2p
